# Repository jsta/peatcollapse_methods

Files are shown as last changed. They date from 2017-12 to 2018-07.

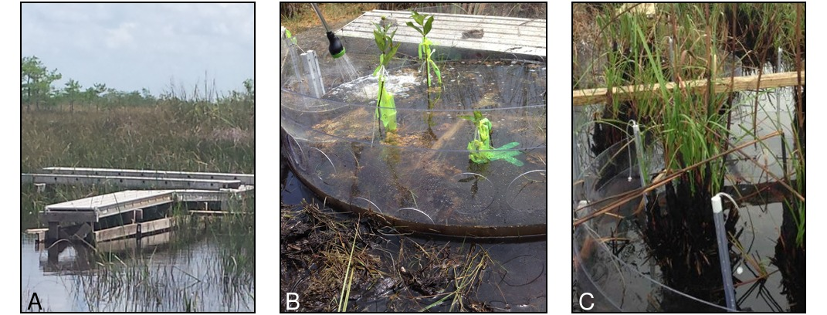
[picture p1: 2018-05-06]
images/02_photos.png

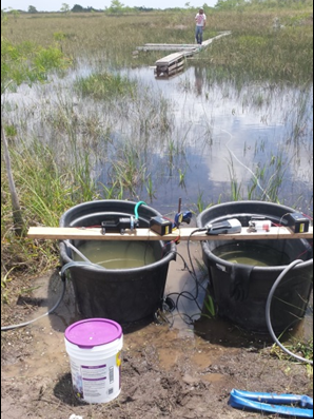
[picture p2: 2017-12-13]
images/mixing_chambers.png

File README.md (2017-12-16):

# In-situ simulation of sea-level rise impacts on coastal wetlands using a flow-through mesocosm approach 



## Dependencies

### System

 * imagemagick

 * GNU make
 
 * FreeCAD
 
## R packages

 * svglite
	
 * ggplot2
	
 * cowplot
 
 * dplyr

## Build

In a terminal from the root directory run:

`$ make all`

## Features

See CAD drawings at /figures/tech_diagram/

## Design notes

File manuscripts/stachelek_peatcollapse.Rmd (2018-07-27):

---
title: In situ simulation of sea-level rise impacts on coastal wetlands using a flow-through mesocosm approach

# Use letters for affiliations
author:
  - name: Joseph Stachelek
    affiliation: a
  - name: Stephen P. Kelly
    affiliation: b
  - name: Fred H. Sklar
    affiliation: b
  - name: Carlos Coronado-Molina
    affiliation: b
  - name: Tiffany Troxler
    affiliation: c,d,e
  - name: Laura Bauman
    affiliation: c
address:
  - code: a
    address: Department of Fisheries and Wildlife, Michigan State University, East Lansing, MI, USA
  - code: b
    address: South Florida Water Management District, Everglades Division, West Palm Beach, Florida
  - code: c
    address: Department of Biological Sciences, Florida International University, Miami, Florida
  - code: d
    address: Southeast Environmental Research Center (SERC), Florida International University, Miami, Florida
  - code: e
    address: Sea Level Solutions Center, Florida International University, Miami, Florida

# For footer text  TODO(fold into template, allow free form two-authors)
lead_author_surname: Stachelek

# Place DOI URL or CRAN Package URL here
doi: "DOI: 10.1111/2041-210X.13028"

# Abstract
abstract: |
  The impact of sea level rise (SLR) on coastal wetlands is dependent on the net effects of increased inundation and saltwater intrusion. The need for accurate projections of SLR impacts has motivated several experimental mesocosm studies aimed at detailed investigations on wetland biogeochemical cycling. However, the degree with which they accurately reproduce field conditions remains unknown because they have primarily been laboratory based using relatively small sediment volumes (10–200 L) treated over short time periods. 
  \newline
  \newline
  As a first step towards addressing these issues, we present a novel mesocosm device and portable methodology for long-term SLR simulation via in situ saltwater additions to relatively large sediment volumes (approximately 1,000 L). The device (chamber) consists of two interlocking polycarbonate cylinders with an internal diameter of 1.4 m. Each cylinder has holes drilled in the side to facilitate water exchange. The outer cylinder (collar) can be rotated to one of two possible positions. The first position produces alignment of the inner cylinder holes with the collar holes, whereas the second position offsets the holes to eliminate water exchange and contain salt additions (doses). 
  \newline
  \newline
  Our device design and dosing scheme produced higher porewater salinities in the sediments of treatment mesocosms relative to control mesocosm sediments. In addition, we observed low incidence of elevated porewater salinity outside of the chamber walls and no measurable salt contamination of control plots. 
  \newline
  \newline
  Widespread SLR simulations in a variety of geographical settings, whether with our proposed design or some other design, would likely help reduce some of the general uncertainties regarding the sensitivity of coastal wetlands to SLR and saltwater intrusion.

Optional: Acknowledgements
acknowledgements: |
 We acknowledge funding from Florida Sea Grant (R/C-S-56) as well as  field  assistance  from Michelle  Blaha,  Fabiola  Santamaria,  Ryan  Stolee,  Oliver  Ljustina,  and  Marbelys  Garriga.  The  authors  declare  no  conflict  of  interests.  This  is  publication  number  13  of  the  Sea  Level  Solutions  Center  and  869  of  the  Southeast  Environmental  Research Center in the Institute of Water and Environment at Florida International University.

# Optional: One or more keywords
keywords:       
   - climate change
   - marsh
   - salinity
   - sea level

# Font size of the document, values of 9pt (default), 10pt, 11pt and 12pt
fontsize: 12pt

# Optional: Force one-column layout, default is two-column
one_column: false

# Optional: Enables lineno mode, but only if one_column mode is also true
#lineno: true

# Optional: Enable one-sided layout, default is two-sided
#one_sided: true

# Optional: Enable section numbering, default is unnumbered
#numbersections: true

# Optional: Specify the depth of section number, default is 5
#secnumdepth: 5

# Optional: Skip inserting final break between acknowledgements, default is false
skip_final_break: true

# Optional: Bibliography 
bibliography: pinp

# Optional: Enable a 'Draft' watermark on the document
watermark: false

# Customize footer, eg by referencing the vignette
footer_contents: "In-situ SLR simulation"

# Produce a pinp document
output: pinp::pinp

# Required: Vignette metadata for inclusion in a package.
vignette: >
  %\VignetteIndexEntry{YourPackage-vignetteentry}
  %\VignetteKeywords{YourPackage, r, anotherkeyword}
  %\VignettePackage{YourPackage}
  %\VignetteEngine{knitr::rmarkdown}
---

```{r setup, include=FALSE}
knitr::opts_chunk$set(echo = FALSE, fig.path = "../figures/", dpi=300, fig.height=3, fig.width=3, out.width="9cm")
```

<!-- \thispagestyle{firstpage} -->
<!-- \restoregeometry -->

## INTRODUCTION

Tide gauge records and satellite altimetry measurements clearly show
evidence of global sea level rise (SLR) from the late 19th century to
present \citep{church_sea-level_2011}. In addition, recent modelling
efforts have projected an increasing rate of global SLR into the future
\citep{rahmstorf_semi-empirical_2007}. One important aspect of SLR is
that it is not uniform. Rather, the sea level experienced along a given
coastal area is a function not only of the magnitude and acceleration of
global sea levels but also their combination with regional ocean
currents, teleconnection patterns, and patterns of glacial isostatic
adjustment \citep{park_accelerated_2015, clark1978global}. As a result, some locations may experience minimal SLR, whereas others could experience additional SLR of as much as 0.6 m by 2060 \citep{zhang_assessment_}. \newline \indent Another important aspect of
SLR is that its potential impact on coastal wetlands is a function not
only of increased hydroperiods but also of elevated salinity
\citep{SpaldingInteractiveeffectshydrology2007}. Each of these
mechanisms is likely to have specific effects on biogeochemical
feed-backs, carbon cycling, and wetland plant adaptation
\citep{Herbertglobalperspectivewetland2015}. In addition, there is
likely to be spatial variability in the response of specific wetland
processes to either increased hydroperiods, elevated salinity, or both.
Overall, these knowledge gaps limit our understanding of spatial
variability in SLR impacts, our ability to forecast these impacts on
coastal wetlands, and our capacity to identify place-specific process
thresholds \citep{cherry_elevated_2009}. \newline \indent Such knowledge
gaps can be addressed in one of several ways. The first and most
straightforward approach is passive monitoring of wetland elevation
trends \citep[e.g.][]{webb_global_2013}. Another approach for addressing
SLR knowledge gaps is simulation modelling \citep[e.g.][]{jiang_analysis_2014}. However, both passive monitoring and
simulation modelling approaches lack the power to confirm specific
process thresholds unless paired with a suite of additional field-based
studies. A final approach, which is the subject of this study, is
experimental manipulation where a set of experimental "treatment" wetland units are exposed to SLR impacts and compared with a set of experimental "controls" \citep[e.g.][]{cherry_testing_2015, LangleyTidalmarshplant2013a, SpaldingInteractiveeffectshydrology2007, craft_climate_change_and_the_fate_of_coastal_wetlands.pdf_2016, LeeDesignConstructionAutomated2016, rasser_role_2009}\. \newline \indent These experimental manipulation approaches are especially powerful because they can provide a specific test of ecological mechanisms across many systems. In practice, these manipulations typically involve isolation of discrete sections of wetland sediment in order to directly lengthen wetland hydroperiods, elevate sediment porewater (interstitial) salinity, or a combination of the two. The physical setup for these manipulations ranges from very simple sediment filled buckets \citep{langley_elevated_2009, rasser_role_2009} to more elaborate weirs \citep{cherry_testing_2015}, tiered cylinder designs \citep{LangleyTidalmarshplant2013a}, and electronically controlled saltwater distributions systems \citep{LeeDesignConstructionAutomated2016}. \newline \indent The motivation for this study was to design an experimental manipulation approach that would alleviate two of our perceived short-comings of existing approaches. Namely, that existing approaches have primarily been laboratory based and that existing approaches have used relatively small sediment volumes (10-200 L) treated over a short time period (weeks-months). As a result, there is some question about whether or not experimental conditions in these prior studies adequately represent natural conditions and whether such short-term studies can be relied on to forecast SLR impacts which take place over the course of years to decades. \newline \indent With these concerns in mind, we designed a manipulation apparatus and experimental protocol with two major design goals (1) maximize the delivery and control of experimental salt doses while (2) introducing greater realism by maintaining experimental units in situ and minimizing disturbance to the local emergent plant and periphyton communities. Here, we describe the features of our design effort relative to our two major design goals. In addition, we report on some tests of our design using a case study set in the Florida Everglades. Our case study specifically tested the hypothesis that the sediment porewater salinity of enclosed wetland
units could be elevated by repeated exposure to salt treatments. This work was completed as part of a larger study to examine the response of coastal peats to saltwater intrusion and to assess whether such intrusion disrupts soil carbon balance and leads to decreased soil
structural integrity \citep[i.e., peat collapse][]{chambersBiogeochemicalEffectsSimulated2014, troxlerChapterCarbonCyclingInPress, cisrerpProgressRestoringEverglades2014}.

## MATERIALS AND METHODS

### Mesocosm Design

Our mesocosm design was inspired by earlier work done by \citet{newman_effect_2004}. The interior (primary) cylinder of each of mesocosm enclosure was constructed of a 0.38 cm ×  0.6 m ×  4.3 m sheet of clear polycarbonate formed into a 1.4 m diameter cylinder (enclosing approximately 1,000 L) using adhesive sealant (Figure 1a). Nine 10 cm holes were drilled in the side of each cylinder located 40 cm above the bottom (Figure 1b) and 30 cm above the bottom (Figure 1c) to facilitate water exchange during high and low water periods respectively (Figure 1c). 

```{r fig1, fig.cap="Mesocosm chamber technical diagram showing (a) the primary cylinder seam, (b) upper water exchange holes, (c) lower water exchange holes, (d) collar locking device, and (e) vertical alignment brackets. Labelled units are in metres", out.width="9cm"}
knitr::include_graphics("../figures/tech_diagram/tech_diagram.png")
```

The  primary  cylinders  were  fitted  with  rotating  polycarbonate  collars  (0.3  m  height)  having  holes  drilled  at  the  same  size  and  alignment as the primary cylinder. In effect, this gave us the ability to rotate the  collar  to  "close "  the  mesocosm  when  delivering  a  salt  dose  and  to "open " the mesocosm to facilitate water exchange. Each collar was fitted with a locking device that could be tightened to ensure minimal surface water exchange during closure (Figure 1d). The locking device was constructed by attaching a high-density plastic (white Starboard) "handle " on either side of a vertical gap in the collar. Two sets of holes were  drilled  through  each  handle  and  fitted  with  long  stainless  steel  bolts. The collar could then be loosened via wing nuts attached to each bolt, rotated to either the open or closed position, and re-tightened to 
lock into place. The vertical position of the collar was maintained via four external "brackets" attached to the exterior of the primary cylinder  (Figure  1e).  Each  bracket  was  constructed  of  high  density  plastic  (white Starboard) with a "groove" to hold the rotating collar.
\newline \indent In an effort to maximize reproducibility, we have made our CAD model  used  to  construct  Figure \ref{fig:fig1} publicly  available  at  https://doi.org/10.5281/zenodo.1117118.  These  files  can  be  opened  in  to  inspect  additional  features  of  our  design  such  as  placement  of  hardware attachments. We have also included a parts list with additional details  regarding  dimensions,  material  quantities,  and  material  dimensions of each mesocosm part (Figure \ref{fig:fig2}).

```{r fig2, fig.cap=" Parts list for construction of a single mesocosm chamber. See CAD drawings in data supplement for more detail", out.width="9cm"}
knitr::include_graphics("../tables/parts_list_trim.png")
```

### Saltwater delivery protocol

We  anticipate  that  most  study  designs  will  include  "treatment"  mesocosms,  which  are  "dosed"  with  a  saltwater  treatment  at  regular intervals, and "control" mesocosms, which are exposed to an ambient water (fresh or brackish) treatment. The exact details surrounding delivery of these saltwater doses will be dependent on  the  layout  and  location  of  each  study  site.  For  example,  saltwater additions in the experimental manipulations by \citet{craft_climate_change_and_the_fate_of_coastal_wetlands.pdf_2016}  were  directly  pumped  from  an  adjacent  tidal  inlet.  Given  that such a setup is not feasible in all situations, we developed a method to deliver portable salt doses irrespective of nearby saltwater sources. Briefly, our protocol makes use of locally sourced freshwater or brackish water combined with a commercial aquarium  salt  mix  (Instant  Ocean,  Blacksburg,  VA,  USA)  prepared  in  400 litre tanks \citep[see][for a similar approach]{LeeDesignConstructionAutomated2016}. Rather than  adding  an  exactly  prescribed  saltwater  dose,  we  devised  a  dosing schedule, which was based on water levels and salinity at each  site,  by  solving  the  following  series  of  mass  balance  equations for the volume of dose-water to be added to each mesocosm (Vb):

\begin{equation}
  \begin{aligned}
S_{f} = \frac{M_{a} + M_{b}}{V_{a} + V_{b}}\\
M_{b} = S_{b} x V_{b}
       \label{eqn:example} 
  \end{aligned}
\end{equation}

where Sf represents the final salinity of the on-site (ambient) and dose water mixture, whereas Ma and Va represent the salt mass (g) and volume (L) of the ambient water within each mesocosm. Variables marked with the subscript b represent equivalent components of the dosing water volume. For example, at one of our case study sites (see below), we fixed Sb
 at 55 and Sf at 20. We could  then  solve  the  above  set  of  mass  balance  equations  by 
adjusting  the  dosing  water  volume  (Vb).  The  rationale  for  our  simple  mass  balance  approach  is  that  we  assume  our  ambient-dose water mixture simple replaces existingporewater as a result of density-driven flow rather than accounting for convective 
diffusion.
\newline \indent We  delivered  saltwater  additions  to  the  treatment  mesocosms  and  ambient  water  additions  to  control  mesocosms  from  elevated  boardwalks   running   alongside   each   mesocosm   (Figure   2a).   We   used a submersible bilge-style pump (Rule, Xylem Inc., USA) to deliver doses at a maximum rate of approximately 32 l/min (500 gph). However, the actual flow rate was likely less given the distance and flow restrictions imposed by the dosing apparatus. The outlet hose was fitted with a spreader device, which was constructed by drilling holes into a short length of Polyvinyl chloride (PVC), in order to split the large output stream into twelve smaller streams. This design was intended to maximize mixing with ambient site water while minimizing scouring of sensitive benthic periphyton. Finally, emergent plants were  briefly  sprayed  with  ambient  water  following  dosing  to  avoid  
burn from salt spray.

## CASE STUDY

We  tested  our  mesocosm  design  and  experimental  protocol  in  a  case  study  at  two  sites  within  Everglades  National  Park,  Florida,  USA. One site was located within an area of freshwater wetlands, whereas  the  second  site  was  located  within  an  area  of brackish  wetlands.  Neighbouring  water  level  monitoring  gauges  indicate  that the freshwater and brackish wetland sites have annual hydro-periods of approximately 312 and 184 days respectively. Patterns of  inundation  at  each  site  were  intermittent  but  not  synced  on  a  regular (e.g., tidal) cycle. 
\newline \indent At each site, we deployed a total of 12 mesocosm chambers by inserting  them  approximately  15  cm  into  the  sediment  (Figure 3b).  We  used  an  unbalanced  design  that  included  6  salt-treated  mesocosms, 6 control mesocosms (treated with ambient site water), and 4 nonchamber control plots. The purpose of the nonchamber controls was to assess whether the chambers themselves influenced the experimental units over time. 
\newline \indent We assessed the overall performance of our mesocosm design and dosing protocol at three points in time following each monthly dosing event: immediately following dosing, the following day, and 5    days  post  dosing.  Our  primary  metric  for  assessment  was  the  relative difference in soil porewater salinity in salt-treated chambers versus control (treated with ambient water) chambers the day after dosing. To this end, we installed three porewater wells (i.e., "sippers") within the interior of each chamber and two porewater wells on the outside of each chamber (Figure 3c). Wells were constructed of 1-m sample tubes inserted to a depth of 15 cm. Sample tubes  were  constructed  of  flexible  Tygon®  tubing,  sealed  with  teflon  tape,  and  protected  with  a  slotted  PVC  sleeve.  Sampling  took place for salinity, temperature, and pH via handheld probes (YSI, Inc.) by purging one length of the sipper tubing and collecting  duplicate  samples. 

```{r fig3, fig.cap="Site photographs showing (a) elevated dosing boardwalks, (b) close-up of deployed mesocosm, and (c) sampling well installation"}
knitr::include_graphics("../images/02_photos.png")
```

We present the results of samples collected the day after dosing because we expected that this was long enough to ensure that any flow down the sides of the installed sampling apparatus would be  mixed  with  the  surrounding  porewater  but  not  so  long  that  porewater would be excessively diluted. We quantified postdosing salt retention/dilution in more detail as part of a pilot experiment. This  pilot  experiment  involved  outfitting  a  single  mesocosm  with  a more comprehensive array of porewater wells at many different distances  and  sampling  at  a  finer  temporal  resolution.  Here  we  present  the  results  of  our  mesocosm  design  and  monthly  dosing protocol tests over a yearly period from October 2014 to October 2015.

## RESULTS

We  found  that  our  long-term  dosing  experiment  was  successful  in  raising  porewater  salinities  above  ambient  (Figure \ref{fig:fig4}).  At  the  fresh-water  wetland  site,  the  salinity  of  the  porewater  was  2.9  ±   0.8  and  0.3  ±    0.1  for  the  treatment  and  control  chambers  respectively  (Figure 4a).  At  the  brackish  wetland  site,  the  salinity  of  the  porewater  was  15.3  ±    1.9  and  10.3  ±    1.9  for  the  treatment  and  control chambers respectively (Figure 4b). We observed few differences between our control mesocosm chambers and our nonchamber control plots  (Figure \ref{fig:fig4}).  This  suggests  that  the  mesocosms  by  themselves  were not directly impacting the experimental units with respect to porewater salinity. Our results were consistent with our hypothesis that indeed the porewater salinity of enclosed wetland units can be elevated by repeated exposure to salt treatments.

```{r fig4, fig.cap="Difference between treatment, control, and nonchamber-control porewater salinities at our (a) freshwater wetland site and (b) brackish wetland site"}
knitr::include_graphics("../figures/03_chem-ts.png")
```

```{r fig5, fig.cap="Fine-scale dilution profile of salt additions to a treatment mesocosm"}
knitr::include_graphics("../figures/04_dilution-profile.png")
```

```{r fig6, fig.cap="Comparison between porewater salinity measured in the outside and inside-chamber sampling wells at the freshwater and brackish wetland sites. Treatment and control measurements are coloured following Figure \ref{fig:fig4}"}
knitr::include_graphics("../figures/05_chamber-leakage.png")
```

Although our design was successful in raising the porewater salinity of our treatment mesocosms over the long-term, the results of our pilot study indicate that a typical salt dose is contained within the sediment porewater of our chambers for only about 5 days, returning to approximately background levels at that point (Figure \ref{fig:fig5}). Despite  the  fact  that  porewater  salinities  following  individual  salt  doses  remained  elevated  for  a  relatively  short  time  period,  our  mesocosm  design  was  successful  in  minimizing  the  movement  of  
saltwater  additions  through  the  chamber  walls  (Figure \ref{fig:fig6}).  At  both  the freshwater and brackish wetland sites, although porewater salinity  measured  in  the  outside
  wells  of  the  treatment  mesocosms  was  slightly  elevated  above  ambient,  there  was  no  discernable  difference between the outside and inside porewater well salinity measurements  in  the  control  chambers.  In  contrast  to  anecdotal  reports from previous studies, our control chambers were not contaminated with salt.

## DISCUSSION

We  believe  our  mesocosm  design  and  experimental  protocol  met  our  design  goals  of  (1)  maximizing  delivery  and  control  over  experimental  salt  doses  and  (2)  introducing  greater  realism  to  experimental manipulations. In the following discussion, we identify  the  specific  features  of  our  design  that  serve  to  meet  these  design goals while contrasting our design choices with that of prior studies.

### Simulation effectiveness

In  our  view,  the  primary  requirement  of  an  effective  mesocosm  design  is  that  salt  additions  are  contained  within  experimental  treatment units as much as possible and do not "leak" into the surrounding  environment.  Although  the  performance  of  our  design in  this  respect  was  not  perfect  (i.e.,  our  mesocosms  did  not  perfectly  contain  salt  additions),  the  extent  to  which  our  mesocosms  were  successful  in  elevating porewater  salinity  in  the  treatment  mesocosms  suggests  that  our  design  was  largely  effective.  For  example,  in  our  brackish  wetland  treatment  we  observed  that  our mesocosms maintained elevated porewater salinities around 15 approximately  24  hr  after  dosing  when  surface  water  salinities  had  been around 20. Surprisingly, few prior studies have reported porewater  salinity  measurements  in  their  experimental  units  relative  to  dose  (surface  water)  salinity.  One  exception  is  \citet{LeeDesignConstructionAutomated2016} where  they  report  adding  an  experimental  dose  with  a  salinity  of  around 10 and measuring porewater salinities of <3. In some ways, both  our  findings  and  the  findings  of  \citet{LeeDesignConstructionAutomated2016}  are  a  consequence of an in situ design where vertical porewater movement is unbounded rather than a laboratory-based experimental design where doses are wholly contained. \newline \indent We  attribute  some  of  the  exceptional  salt  retention  properties of our mesocosms (e.g., there was little evidence of elevated salinity outside experimental units) to the rotating collar feature of our design. When our rotating collars were in the closed position  the  water  exchange  holes  were  completely  sealed.  The  evidence for this is that we did not observe elevated salinity in the surface  water  outside  the  chambers  or  contamination  of  control  plots  with  salt  (Figure \ref{fig:fig6}).  We  know  from  anecdotal  reports  that  mesocosms  constructed  using  alternative  designs  where  water  exchange  holes  are  merely  plugged  with  rubber  stoppers  \citep[e.g.][]{miller_effects_2001} are subject to much higher probability  of  observing  elevated  salinity  outside  experimental  units (i.e., salt leakage). It is difficult to gather information on this design  aspect  (potential  leakage)  of  prior  studies  because  it  is  most often not reported.

### Simulation realism

In addition to faithfully containing salt additions within experimental
units, we believe that a primary requirement of an effective mesocosm
design is a high degree of simulation realism. To this end, our open
bottom in situ design was meant to simulate slow buildup of salt in the
surficial groundwater as a result of SLR while maintaining natural
drainage conditions. Indeed, the pulsed nature of our salt additions
meant that elevated porewater salinity was maintained for only about 5
days and was not constant. This variability contrasts with the design of many laboratory-based studies that completely isolate experimental units to impose a constant
salt treatment \citep{BrockChangesbioticcommunities2005, LangleyTidalmarshplant2013a}.
Although constantly elevated salinities may be preferable to maximize
treatment effects in the short-term, we designed our experimental
protocol to more realistically mimic the impact of gradual and episodic
ramping of salinity over the long term (years to decades). Ultimately,
our design likely comes at the cost of longer times necessary to observe
a salt dose response, but we believe this is preferable to short-term
simulations where experimental units are completely isolated leading to
rapid salt accumulation. \newline \indent Our expectation that near-term changes in SLR will cause variable and episodic increases in the salinity of shallow porewater and wetland plant root-zones is supported by several lines of observational and experimental evidence. First, in karst or low tidal systems, the response of coastal wetlands to SLR during the transition from a vegetated to open water state can be dependent on variability in seasonal groundwater- surface water exchange \citep{saha_hydrological_2012}. Second, \citet{WestonAcceleratedmicrobialorganic2011a} describe how saltwater intrusion in wetland soils likely occurs in pulses rather than as a constant steady increase. Finally, \citet{craft_climate_change_and_the_fate_of_coastal_wetlands.pdf_2016} specifically contrasted wetland responses to constant (press) and variable (pulse) salinity doses and found that although pulsed doses were transient and short-lived, there were significant impacts on the
composition of the emergent plant community. \newline \indent Another way in which our pulsed design maintains a high degree of simulation realism is the fact that our chambers retained a natural assemblage of flora and fauna. We view this as a substantial improvement over previous
designs because biotic processes have been shown to be critical components of wetland resilience to SLR \citep{mckee_biophysical_2011, morris_responses_2002}. There are three
features of our design that made this possible and set it apart from prior studies. First, our mesocosm chambers were large. Our 1000 L mesocosm chambers are much larger than most previous studies of only 10-200 L. In our study, this meant that all of our experimental units
at the brackish wetland site included intact sawgrass (_Cladium jamaicense_) culms and we frequently observed fauna such as mosquitofish (_Gambusia holbrooki_) moving freely into and out of the chambers (in the open position) at the freshwater wetland site. Second, we took several steps in the experimental protocol to minimize our impact on flora and
fauna including rinsing emergent plants following dosing to avoid burn from salt spray, monitoring soil redox conditions to avoid introducing severely anoxic conditions that exacerbate sulphide stress, and regulating the velocity of dose output to avoid scouring of sensitive benthic periphyton. Finally, the in situ nature of our design likely
increased the realism of our simulations because it minimized physical disturbance of below-ground root material in our experimental units.

## CONCLUSIONS

Ultimately, a successful SLR manipulation design requires a balance of simulation effectiveness and simulation realism. We believe that our rotating collar design gave us a unique ability to strike this balance  as  we  were  effective  in  containing  salt  additions  while  maintaining the conditions necessary for realistic drainage patterns and 
intact biotic communities.
\newline \indent We  tested  our  mesocosm  design  and  experimental  protocol  in two locations during our case study. Unfortunately, a comprehensive  test  of  our  design  in  many  different  settings  is  beyond  the scope of this study. However, our design is not limited to the Everglades system. We envision that our design could be used in a variety of settings including those that experience regular daily tidal cycles. In particular, the height of our chambers could easily be  increased  at  sites  where  mean  high  water  exceeds  the  total  installed  chamber  height  of  our  design  (about  0.3  m).  Although  regular  daily  tidal  cycles  were  not  a  feature  of  our  case  study, water  levels  were  below  the  sediment  surface  throughout  the  late spring period. During these periods we added a standard salt dose volume in proportion to an estimate of sediment pore space volume (soil porosity). In fact, the study by \citet{craft_climate_change_and_the_fate_of_coastal_wetlands.pdf_2016} adopted  a  similar  approach  in  a  location  subject  to  daily  tidal  cycles when they added salt doses only during low tide to facilitate infiltration.
\newline \indent We  hope  that  our  design  will  inspire  others  to  initiate  similar  studies in a variety of geographical settings. Whether with our proposed  design  or  some  other  design,  a  standardized  methodology  would likely help reduce some of the general uncertainties regarding  prediction  of  coastal  wetland  sensitivity  to  SLR  and  saltwater  intrusion.

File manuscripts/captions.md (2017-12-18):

Figure 1: Mesocosm chamber technical diagram showing A) the primary cylinder seam, B) upper water exchange holes, C) lower water exchange holes, D) collar locking device, and E) vertical alignment brackets. Labeled units are in meters.

Figure 2: Site photographs showing A) elevated dosing boardwalks, B) close-up of deployed mesocosm, and C) sampling well installation.

Figure 3: Difference between treatment, control, and nonchamber-control porewater salinities at our A) freshwater wetland site and B) brackish wetland site.

Figure 4: Fine-scale dilution profile of salt additions to a treatment mesocosm.

Figure 5: Comparison between porewater salinity measured in the outside and inside-chamber sampling  wells at the freshwater and brackish wetland sites. Treatment and control measurements are colored following Figure 3.

Table 1: Parts list for construction of a single mesocosm chamber. See CAD drawings in data supplement for more detail.

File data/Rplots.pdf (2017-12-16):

brackish

freshwater

control

treatment

control

treatment

inside

outside

inside

outside

inside

outside

inside

outside

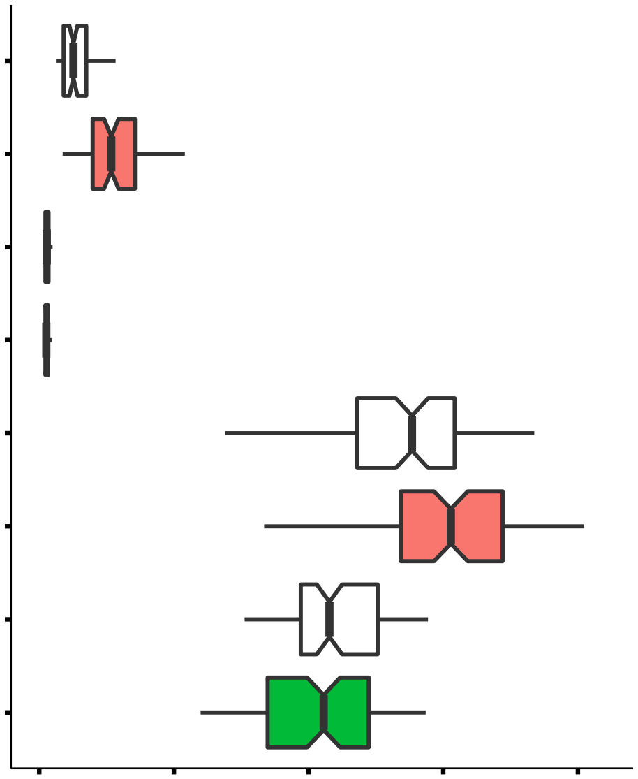
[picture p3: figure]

0 | 5 | 10 | 15 | 20
| | Salinity

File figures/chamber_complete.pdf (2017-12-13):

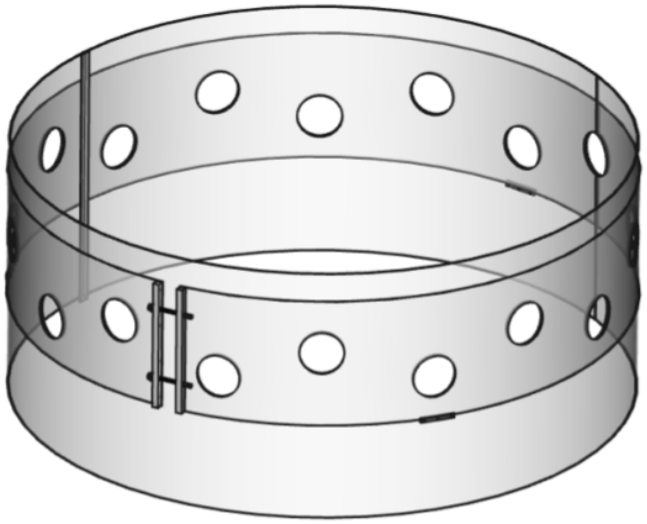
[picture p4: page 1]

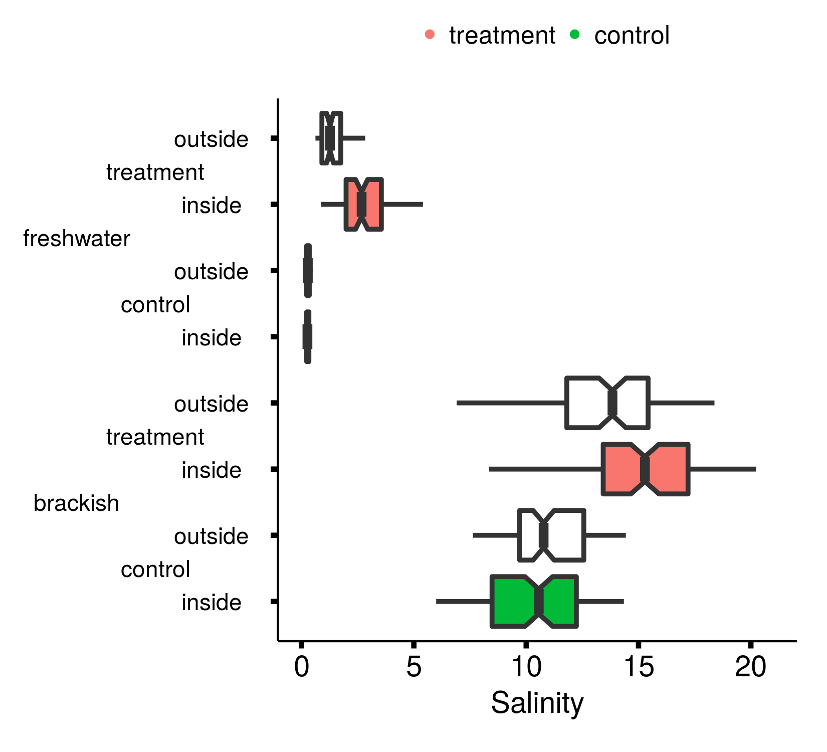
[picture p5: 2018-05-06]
figures/05_chamber-leakage.png

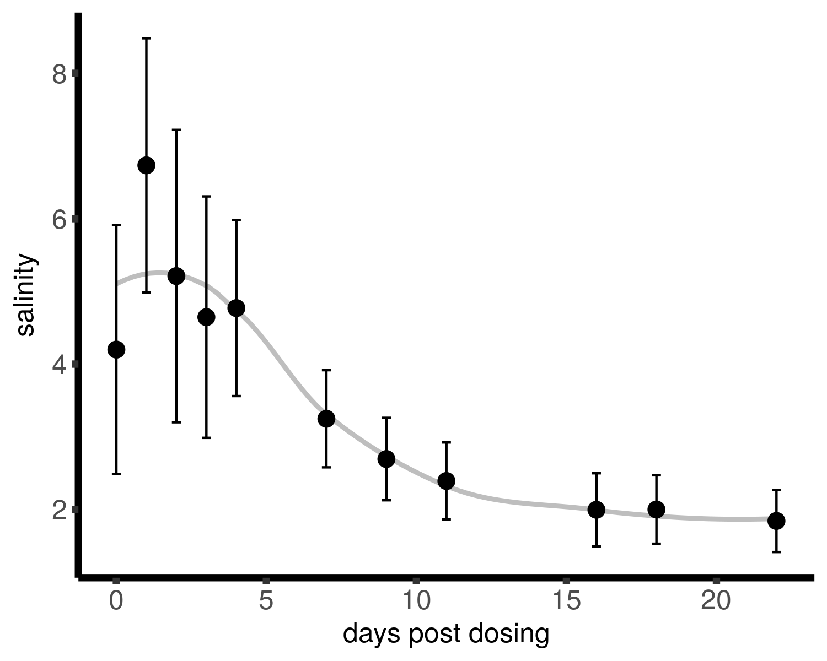
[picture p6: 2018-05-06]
figures/04_dilution-profile.png

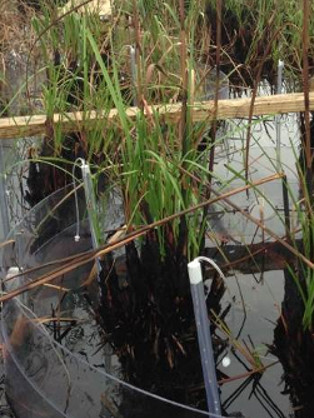
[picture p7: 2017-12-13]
images/field_mesocosm.jpg

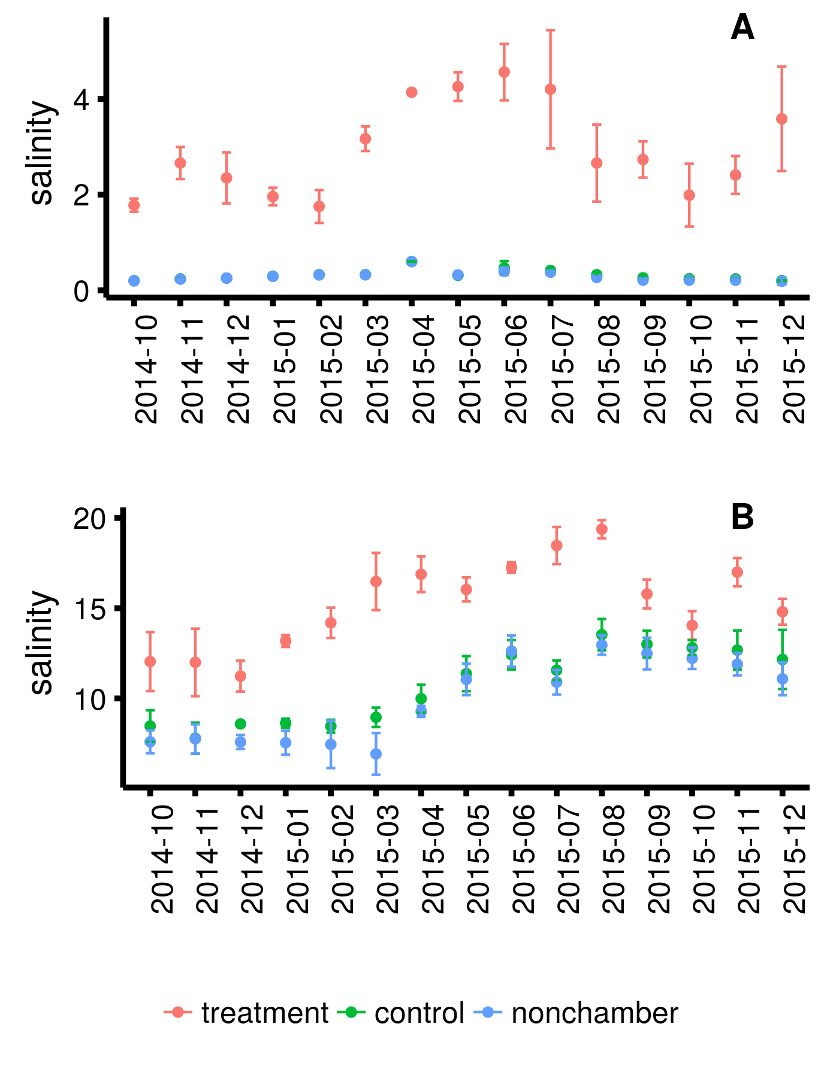
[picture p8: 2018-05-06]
figures/03_chem-ts.png

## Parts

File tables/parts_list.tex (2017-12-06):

\documentclass[standalone]{article}

\begin{document}
\centering
\begin{tabular}{llcc}
\textbf{name} & \textbf{description} & \textbf{dimensions (lwd, m)} & \textbf{quantity} \\ 
\hline
Primary cylinder body & clear polycarbonate & 4.270 * 0.60 * 0.0038 & 1 \\
Primary cylinder seam & clear polycarbonate & 0.020 * 0.60 * 0.0038 & 1 \\
Primary cylinder seam adhesive &            & & \\
Rotating collar body & clear polycarbonate  & 4.270 * 0.30 * 0.0038 & 1 \\
Collar fastener posts & PVC or equivalent   & 0.015 * 0.30 * 0.0150 & 2 \\
Collar fastener post attachments & M3 standoffs & & \\
Collar fastener bolts & stainless steel, M10 x 100 & & 2 \\
Wingnuts & stainless steel, M10 & & 2 \\
Collar bracket body & PVC or similar        & 0.080 * 0.01 * 0.0080 & 3 \\
Collar bracket attachments & M2.5 standoffs & & 9 \\
\end{tabular}
\end{document}

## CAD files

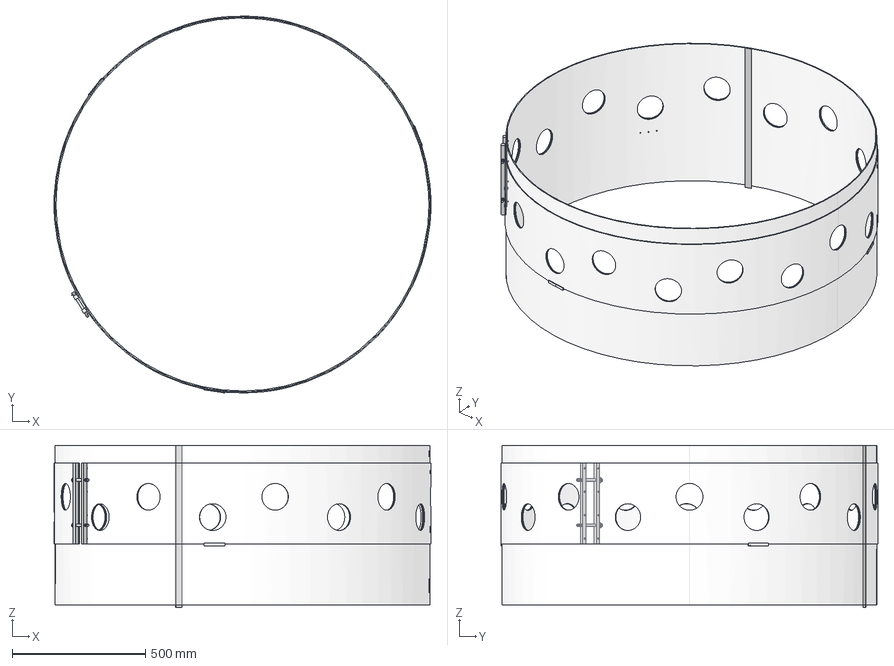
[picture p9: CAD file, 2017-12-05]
figures/tech_diagram/tech_diagram.fcstd
1415.2 x 1415.0 x 610.0 mm
outer-bracket_post_left
outer_bracket_rivets_left
outer-bracket_post_right
outer_sleeve_cut
outer_bracket_rivets_right
outerbracket_bolts
outer-bracket_fasteners_left
outer-bracket_fasteners_right
inner_sleeve_seam
inner_sleeve_cut
brackets

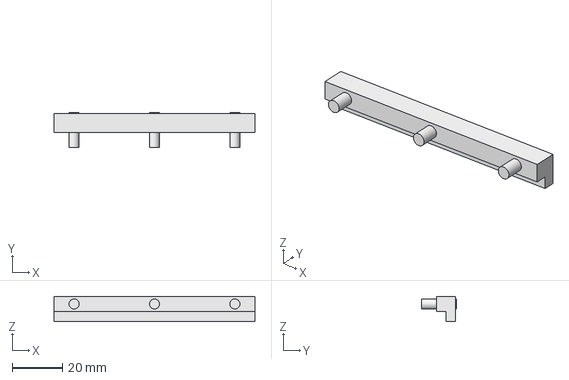
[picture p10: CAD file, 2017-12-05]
figures/tech_diagram/bracket.fcstd
80.0 x 14.0 x 10.0 mm

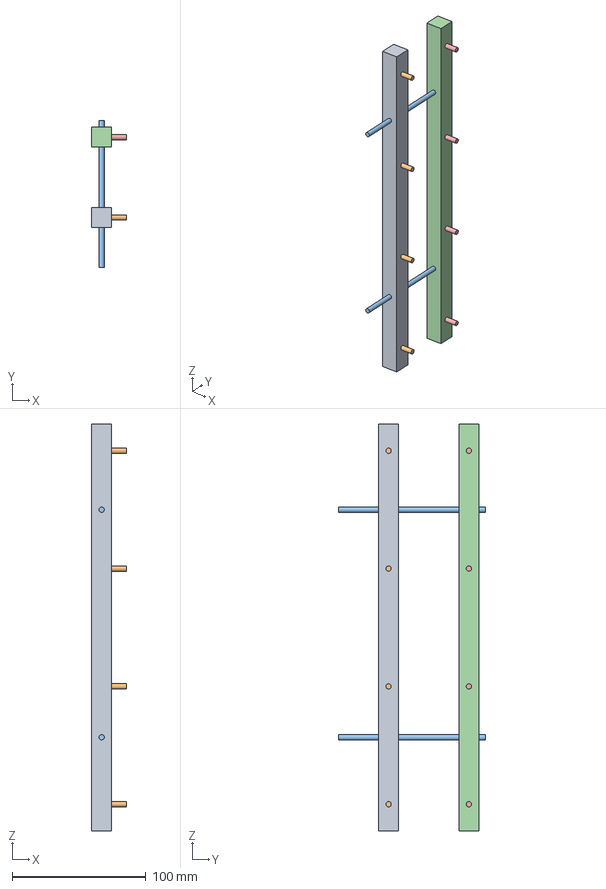
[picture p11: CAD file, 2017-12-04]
figures/tech_diagram/outer_fastener.fcstd
26.0 x 110.0 x 304.0 mm

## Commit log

2017-11-29 save cad drawing
    [tech_diagram.fcstd]
2017-12-04 finish outersleeve
    [tech_diagram.fcstd]
2017-12-04 create outer fastener and bracket
    [bracket.fcstd, outer_fastener.fcstd, tech_diagram.fcstd]
2017-12-05 attach outer fastener to outer sleeve
    [tech_diagram.fcstd]
2017-12-05 add threaded screws to outer fastener
    [tech_diagram.fcstd]
2017-12-05 add outerbracket rivets
    [tech_diagram.fcstd]
2017-12-05 add inner sleeve seam
    [tech_diagram.fcstd]
2017-12-05 place first bracket
    [bracket.fcstd, tech_diagram.fcstd]
2017-12-05 add bracket polar array
    [tech_diagram.fcstd]
2017-12-15 use better boardwalk image
2017-12-15 stash boardwalk image
2018-05-06 resize to be under 7cm width
